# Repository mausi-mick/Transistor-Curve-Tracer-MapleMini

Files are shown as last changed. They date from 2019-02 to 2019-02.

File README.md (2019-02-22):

# Transistor-Curve-Tracer-MapleMini

This project based on the super project "Transistor Curve Tracer" from Peter Balch :
https://www.instructables.com/id/Transistor-Curve-Tracer/  

I ported the software from the 8-bit Arduino platform ( hardware: Arduino Pro Mini ) to 32 bit STM32duino (hw: MapleMini).

For me was the MapleMini the best choice: cheap, quick, enough program-space, more accessible port-pins as the Arduino Uno/Nano/... and more flexibility and accuracy :

more than 5 ADC's with 12-bit resolution, 2 SPI's/, more than 2 ISR-Pins (for the encoders) and USB-socket for programming and supply. 
Also the 3.3 V port-voltage was favourable for connections to the ILI9341-spi-tft-display/touch.

For more information about MapleMini look here: https://www.stm32duino.com/
or about this project:  https://www.stm32duino.com/viewtopic.php?t=4269

Therefore I had the possibility to integrate other features:

- integration of two rotary encoders (on isr) for a more comfortable changing of the parameters, a dual DAC (MCP4822) with the same 12-bit resolution as the ADC's on the MapleMini.
- possibility to save the parameters in the internal EEPROM
- possibility compare similar or complementary devices on the same screen
- changing x-scale for diodes/zeners (0,1,2,3,4,6,12,24V) (0: starts with 24V and search the optimal scale)
- changing y-sacle for diodes from 0...10mA  to 0...50mA
- changing y-scale for MosFETs/jFETs automatic depending on max. IDss from 50mA to 10mA or 50mA to 100mA
- changing x-scale for n-jFETs from 12V (default), 6V, 4V, 3V, 2V.

The schematic of the tracer is different from Peters version:

I use switches to connect the Emitter/Source/Cathode respectively Collector/Drain/Anode to +/- supply-voltage only while measuring - most time the DUT is only with the base connected, Emtter / Collector are isolated.
At first I tested it with a dual toggle switch, than with mechanical relais, than I changed to  PhotoMosRelais because of less space on the board and less supply-current( 40ma/5V -> 2-5mA/3.3V). So the MapleMini-ports can drive the PhotoMosRelais direct.

As amplifier to drive the Emitter/Source ... Collector/Drain I made another design.
Peter used a LM358 standard dual amplifier with emitter-followers, but I think it was difficult to make it stable and there was a big drop on the positive rail.
Therefore I searched and tested some other amplfiers with drive capacibility of more than 50mA, among others NE5532 , L2272 and TCA0372.
The TCA0372 was the best in relation to stability and to low drop on the supply (r-to-r) at 50mA.
I use only one amplifier of the TCA0372 with gain = +3 (default).
The output of the TCA0372 can manage more than 100mA, the negative supply-voltage I put down to about -3V, because the TCA0372 is not a real rail-to-rail-amplifier at this currents. The negative supply near -3V is generated with a charge-pump (from+3.3V).
With the U-DAC (MCP4822) I can generate 0...12V similar the version from Peter.
As amplifier for the base-current/gate-voltage I use a LT1013 dual amplifier, because it's a R to R and can work up to max. 44V.
The TCA0372 has a normal supply-voltage from 12.6V, changing to about 26V for measuring zeners with Vz > 12V and <= 24V. Therefore I have to change the gain of the TCA0372 to +6 (V-DAC-max  (=4.095V) * 6 >=24V).
For measuring nJFETS in the ohmic-region (< Vpinch) I can switch the x-scale at the display from 12V ... to 2V.
Between 2V and 4V the gain of the TCA0372 is switched from 3 to 2, the V-DAC MCP4822 works than from 0...2.047V with step = 0,5mV.  

The LT1013 has a positive supply-voltage from around 26V, a negative supply from -12v via a LM317L and ICL7662 charge-pump.
I need the negative supply for the gates from nJFET's and depletion-mode-nMOSFET's, the positive supply > 12V for the gates from 
p-JFET's (I think it exist only one depletion-mode-pMOSFET-chip!).

The gain of the opamp's of the LT1013 can be changed from +6 to -6 with two PhotoMosRelais, or better 
over the relais I can select the opamp with the gain +6 or -6.

For npn/pnp and MosFets the I-DAC here works from 0... 2.047 V to generate 0 ... + 12 V with gain = +6 or
with gain = -6  to generate 0 ... - 12 V gatevoltage for nJFET's,
for pJFET's the I-DAC works from about 2.048 ... 4.095 V to generate gatevoltage from +12 ... +24 V for
pJFET with gain +6.

The current is limited to max 50mA . only for JFET's/MOSFET's it can go in a second step up to about 100mA.

The software is developed with the ARDUINO IDE 1.8.4, STM32duino is about one year (2017) old, but I think the newest version would work to.

You have to load  Bootloader 2.0 (20k RAM, 120k Flash) in MapleMini.

The main components are:

- ILI9341 TFT-SPI-Display 2.8" with Touch ca 6.70 €
- MapleMini                                  3.60 €
- DACMCP4822                                 3.20 € 
- AQY212 6x                                  6.00 €
- LT1013                                     1.40 €
- TCA0372                                    1.10 €
- MT3608 3x                                  2.00 €
- Rotary Encoder 2x                          2.00 €
- nMOS switch    7x                          2.00 €    
- ICL7662 (-12V) + TSP490603(-5/-3.3V)       4.00 €
-                           SUM:            32.00 €
+ resistors, capacitors, diodes, test-sockets,                                          
+ pcb's, wire, zinn, sockets, battery, chassis ...     

The hardware is nearly finsihed, the software is growing !

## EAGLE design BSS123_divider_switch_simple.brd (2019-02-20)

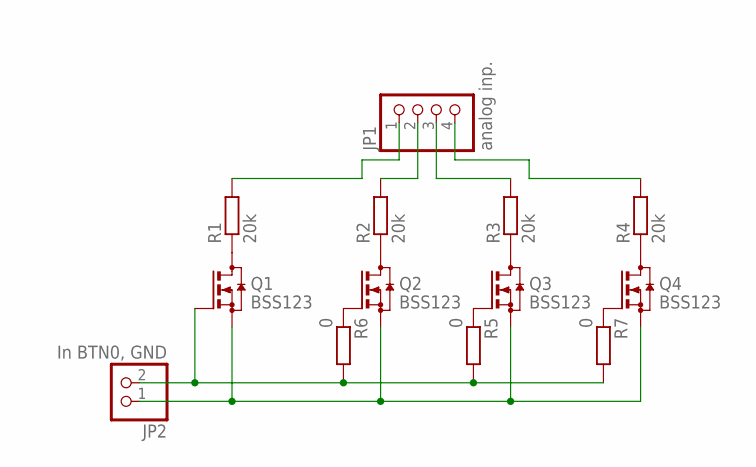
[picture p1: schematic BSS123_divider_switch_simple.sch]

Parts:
JP1: analog inp.; 1X04
JP2: In BTN0, GND; 1X02
Q1, Q2, Q3, Q4: BSS123; SOT23
R1, R2, R3, R4: 20k; R1206
R5, R6, R7: 0; R1206

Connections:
unnamed: Q1.3 (D), R1.1
unnamed: Q2.3 (D), R2.1
unnamed: Q3.3 (D), R3.1
unnamed: Q4.3 (D), R4.1
unnamed: Q4.1 (G), R7.1
unnamed: JP2.1, Q1.2 (S), Q2.2 (S), Q3.2 (S), Q4.2 (S)
unnamed: JP1.1, R1.2
unnamed: JP1.2, R2.2
unnamed: JP1.3, R3.2
unnamed: JP1.4, R4.2
unnamed: Q2.1 (G), R6.1
unnamed: Q3.1 (G), R5.1
unnamed: JP2.2, Q1.1 (G), R5.2, R6.2, R7.2

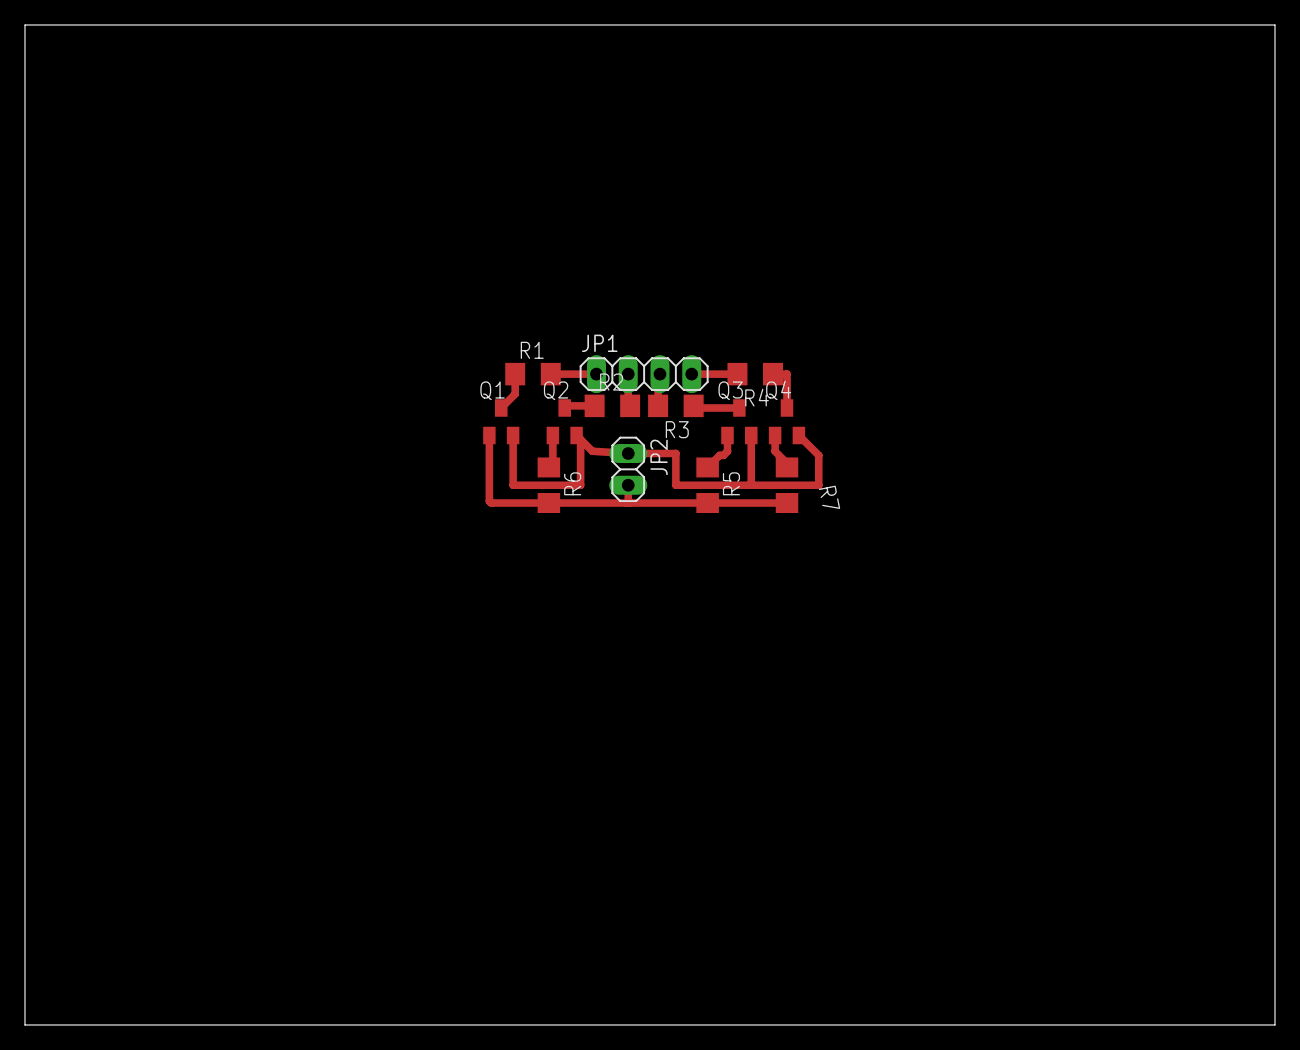
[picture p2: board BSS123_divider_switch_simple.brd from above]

Board: 2 copper layers, 100.0 x 80.0 mm, 13 parts (0 on the bottom side), 13 nets.

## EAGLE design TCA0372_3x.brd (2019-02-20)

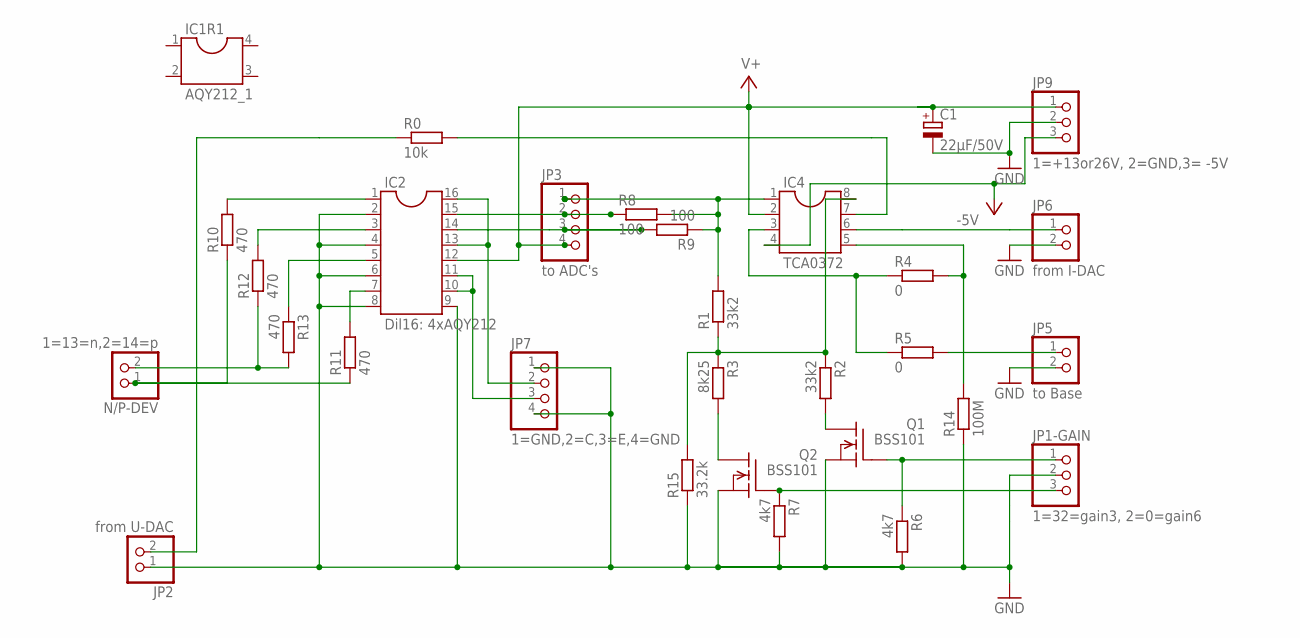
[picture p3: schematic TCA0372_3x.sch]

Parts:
C1: 22µF/50V; E5-10,5
IC1R1: AQY212_1; SOCKET-04
IC2: Dil16: 4xAQY212; SOCKET-16
IC4: TCA0372; SOCKET-08
JP1-GAIN: 1=32=gain3, 2=0=gain6; 1X03
JP2: from U-DAC; 1X02
JP3: to ADC's; 1X04
JP5: to Base; 1X02
JP6: from I-DAC; 1X02
JP7: 1=GND,2=C,3=E,4=GND; 1X04
JP9: 1=+13or26V, 2=GND,3= -5V; 1X03
N/P-DEV: 1=13=n,2=14=p; 1X02
Q1, Q2: BSS101; TO92
R0: 10k; 0207/7
R1, R2: 33k2; 0207/7
R3: 8k25; 0207/7
R4, R5: 0; 0207/7
R6, R7: 4k7; 0207/7
R8, R9: 100; 0207/7
R10, R11, R12, R13: 470; 0207/7
R14: 100M; 0207/7
R15: 33.2k; 0207/7

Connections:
-5V: IC4.4, JP9.3
GND: C1.-, IC2.2, IC2.4, IC2.6, IC2.8, IC2.9, JP1-GAIN.2, JP2.1, JP5.2, JP6.2, JP7.1, JP7.4, JP9.2, Q1.1 (S), Q2.1 (S), R6.2, R7.2, R14.1, R15.1
unnamed: IC4.5, R4.2, R14.2
unnamed: IC2.15, JP3.2, R8.1
unnamed: IC4.7, R0.2
unnamed: IC2.7, R11.2
unnamed: Q1.3 (D), R2.2
unnamed: Q2.3 (D), R3.2
unnamed: JP1-GAIN.1, Q1.2 (G), R6.1
unnamed: JP1-GAIN.3, Q2.2 (G), R7.1
unnamed: IC4.6, JP6.1
unnamed: IC2.3, R12.2
unnamed: IC2.13, IC2.16, JP7.2
unnamed: JP2.2, R0.1
unnamed: IC4.3, R4.1, R5.1
unnamed: IC2.5, R13.1
unnamed: N/P-DEV.2, R12.1, R13.2
unnamed: IC2.1, R10.2
unnamed: N/P-DEV.1, R10.1, R11.1
unnamed: JP5.1, R5.2
unnamed: IC4.1, JP3.1, R1.2, R8.2, R9.1
unnamed: IC4.8, R1.1, R2.1, R3.1, R15.2
unnamed: IC2.10, IC2.11, JP7.3
unnamed: IC2.14, JP3.3, R9.2
V+: C1.+, IC2.12, IC4.2, JP3.4, JP9.1

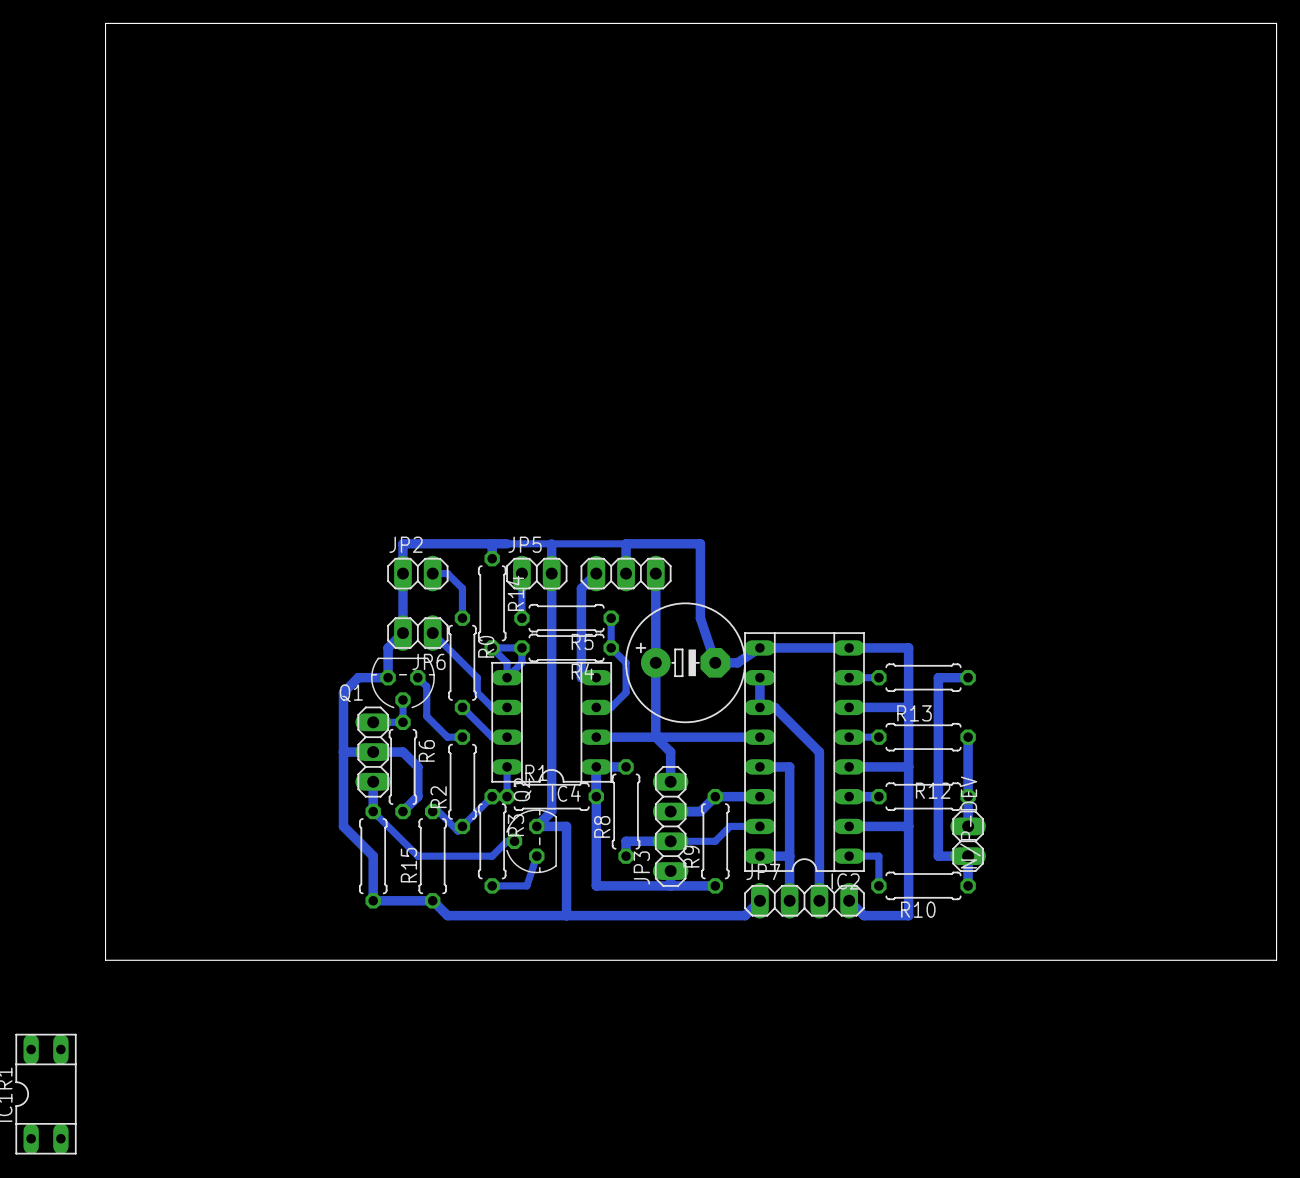
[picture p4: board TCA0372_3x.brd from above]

Board: 2 copper layers, 100.0 x 80.0 mm, 30 parts (0 on the bottom side), 25 nets.

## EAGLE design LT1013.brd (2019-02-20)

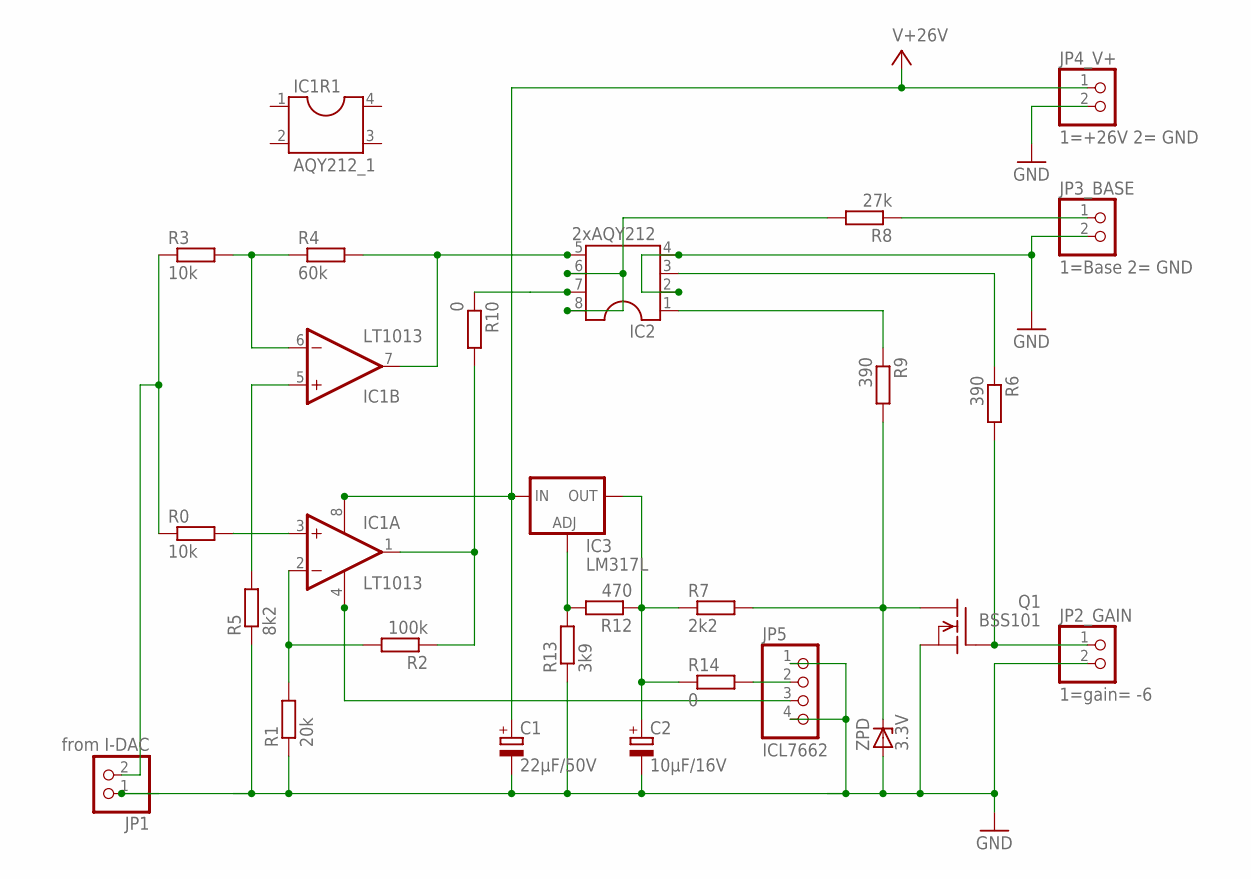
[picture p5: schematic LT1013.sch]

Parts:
C1: 22µF/50V; E5-10,5
C2: 10µF/16V; B45181B
IC1: LT1013; DIL08
IC1R1: AQY212_1; SOCKET-04
IC2: 2xAQY212; SOCKET-08
IC3: LM317L; 317L
JP1: from I-DAC; 1X02
JP2_GAIN: 1=gain= -6; 1X02
JP3_BASE: 1=Base 2= GND; 1X02
JP4_V+: 1=+26V 2= GND; 1X02
JP5: ICL7662; 1X04
Q1: BSS101; TO92
R0, R3: 10k; 0207/7
R1: 20k; 0207/7
R2: 100k; 0207/7
R4: 60k; 0207/7
R5: 8k2; 0207/7
R6, R9: 390; 0207/7
R7: 2k2; 0207/7
R8: 27k; 0207/7
R10, R14: 0; 0207/7
R12: 470; 0207/7
R13: 3k9; 0207/7
ZPD: 3.3V; ZDIO-7.5

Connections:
GND: C1.-, C2.-, IC2.2, IC2.4, JP1.1, JP2_GAIN.2, JP3_BASE.2, JP4_V+.2, JP5.1, JP5.4, Q1.1 (S), R1.1, R5.1, R13.1, ZPD.A
unnamed: IC1.6 (-IN), R3.2, R4.1
unnamed: IC1.2 (-IN), R1.2, R2.2
unnamed: IC1.1 (OUT), R2.1, R10.2
unnamed: IC1.3 (+IN), R0.2
unnamed: IC2.1, R9.1
unnamed: IC1.7 (OUT), IC2.5, R4.2
unnamed: Q1.3 (D), R7.2, R9.2, ZPD.C
unnamed: JP5.2, R14.2
unnamed: JP3_BASE.1, R8.1
unnamed: IC2.6, IC2.8, R8.2
unnamed: JP2_GAIN.1, Q1.2 (G), R6.2
unnamed: JP1.2, R0.1, R3.1
unnamed: IC1.5 (+IN), R5.2
unnamed: IC2.3, R6.1
unnamed: IC2.7, R10.1
unnamed: IC1.4 (V-), JP5.3
unnamed: IC3.1 (ADJ), R12.2, R13.2
unnamed: C2.+, IC3.2 (OUT), R7.1, R12.1, R14.1
V+: C1.+, IC1.8 (V+), IC3.3 (IN), JP4_V+.1

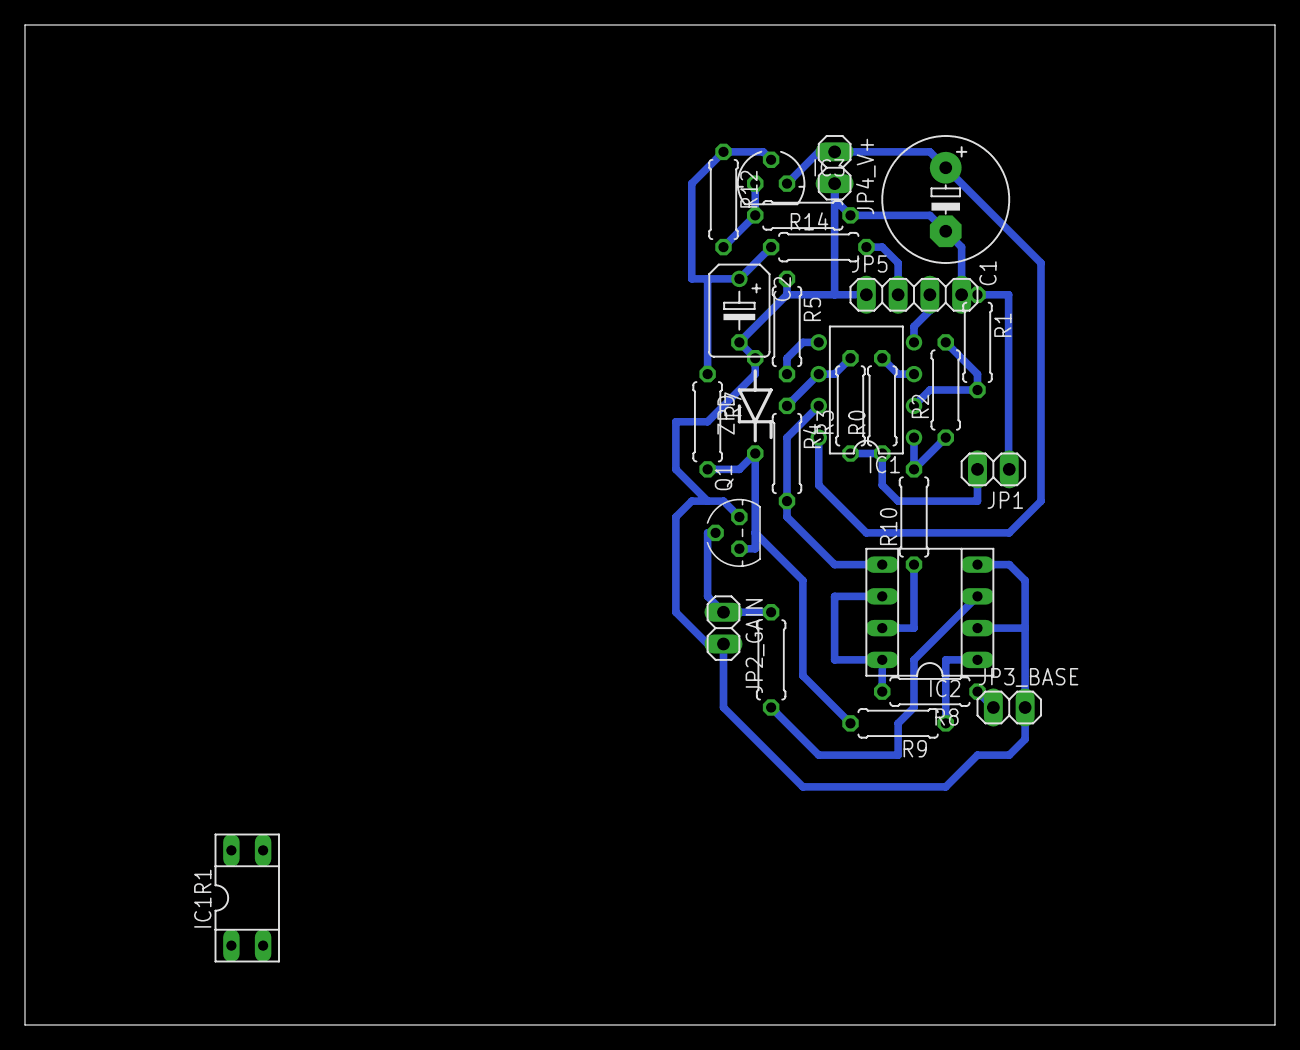
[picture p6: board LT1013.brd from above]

Board: 2 copper layers, 100.0 x 80.0 mm, 27 parts (0 on the bottom side), 20 nets.

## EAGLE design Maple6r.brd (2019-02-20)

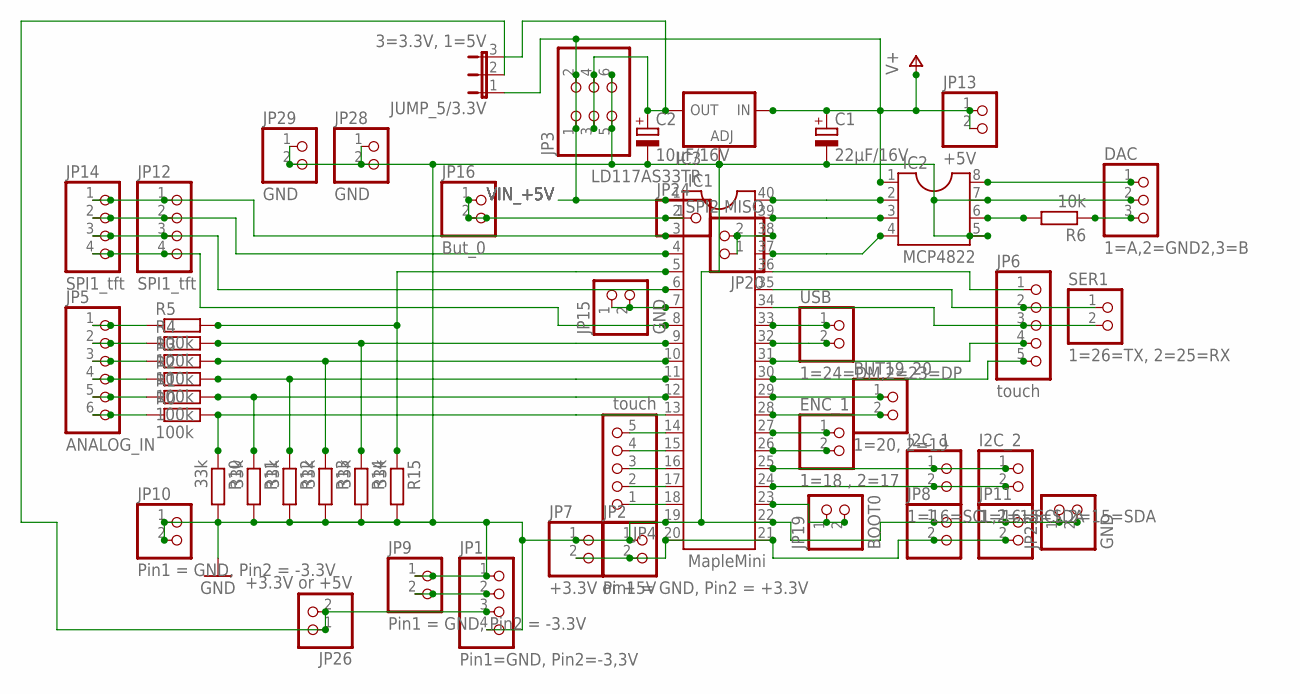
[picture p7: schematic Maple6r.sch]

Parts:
BUT19_20: 1=20, 2=19; 1X02
C1: 22µF/16V; E5-8,5
C2: 10µF/16V; E5-8,5
DAC: 1=A,2=GND2,3=B; 1X03
ENC_1: 1=18 , 2=17; 1X02
I2C_1, I2C_2: 1=16=SCL,2=15=SDA; 1X02
IC1: MapleMini; DIL40
IC2: MCP4822; SOCKET-08
IC3: LD117AS33TR; SOT223
JP1: Pin1=GND, Pin2=-3,3V; 1X04
JP2: Pin1 = GND, Pin2 = +3.3V; 1X02
JP3: PINHD-2X3; 2X03
JP4, JP6: touch; 1X05
JP5: ANALOG_IN; 1X06
JP7, JP26: +3.3V or +5V; 1X02
JP8, JP11: PINHD-1X2; 1X02
JP9, JP10: Pin1 = GND, Pin2 = -3.3V; 1X02
JP12, JP14: SPI1_tft; 1X04
JP13: +5V; 1X02
JP15, JP23, JP28, JP29: GND; 1X02
JP16: But_0; 1X02
JP19: BOOT0; 1X02
JP20: SPI2 MISO; 1X02
JP24: PINHD-1X1; 1X01
JUMP_5/3.3V: 3=3.3V, 1=5V; JP2
R0, R1, R2, R3, R4, R5: 100k; 0207/7
R6: 10k; 0207/7
R10, R11, R12, R13, R14, R15: 33k; 0207/7
SER1: 1=26=TX, 2=25=RX; 1X02
USB: 1=24=DM,2=23=DP; 1X02

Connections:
1_PB10: IC1.3, JP12.1, JP14.1
2_PB2: IC1.4, JP12.2, JP14.2
3_PB0: IC1.5, R5.2, R15.1
4_PA7: IC1.6, JP12.3, JP14.3
6_PA5: IC1.8, JP12.4, JP14.4
7_PA4: IC1.10, R3.2, R13.1
8_PA3: IC1.11, R2.2, R12.1
10_PA1: IC1.12, R1.2, R11.1
11_PA0: IC1.13, R0.2, R10.1
GND: C1.-, C2.-, DAC.2, IC1.19, IC1.22, IC2.5, IC2.7, IC3.1 (ADJ), JP1.1, JP1.4, JP2.1, JP3.5, JP3.6, JP7.1, JP8.1, JP9.1, JP10.1, JP10.2, JP11.1, JP23.1, JP23.2, JP28.1, JP28.2, JP29.1, JP29.2, R10.2, R11.2, R12.2, R13.2, R14.2, R15.2
unnamed: IC1.9, R4.2, R14.1
unnamed: JP5.1, R5.1
unnamed: JP5.2, R4.1
unnamed: JP5.3, R3.1
unnamed: JP5.4, R2.1
unnamed: JP5.5, R1.1
unnamed: JP5.6, R0.1
unnamed: IC1.30, JP6.5
unnamed: IC1.7, JP15.1, JP15.2
unnamed: IC1.32, USB.2
unnamed: IC1.2, JP16.1, JP16.2, JP24.1
unnamed: IC1.31, JP6.4
unnamed: JP1.2, JP9.2
unnamed: ENC_1.1, IC1.27
unnamed: JP1.3, JP26.1, JP26.2, JUMP_5/3.3V.2
unnamed: IC1.38, JP20.1, JP20.2
unnamed: IC1.33, USB.1
unnamed: IC1.36, JP6.1
unnamed: IC1.35, JP6.2, SER1.1
unnamed: IC2.6, R6.2
unnamed: IC1.40, IC2.2
unnamed: IC1.39, IC2.3
unnamed: IC1.14, JP4.5
unnamed: IC1.37, IC2.4
unnamed: IC1.15, JP4.4
unnamed: C2.+, IC3.4 (OUT), JP3.3, JP3.4, JUMP_5/3.3V.3
unnamed: IC1.34, JP6.3, SER1.2
unnamed: IC1.16, JP4.3
unnamed: IC1.17, JP4.2
unnamed: IC1.18, JP4.1
unnamed: BUT19_20.1, IC1.29
unnamed: BUT19_20.2, IC1.28
unnamed: ENC_1.2, IC1.26
unnamed: I2C_1.1, I2C_2.1, IC1.25
unnamed: I2C_1.2, I2C_2.2, IC1.24
unnamed: IC1.23, JP19.1, JP19.2
unnamed: IC1.20, IC1.21, JP2.2, JP7.2, JP8.2, JP11.2
unnamed: DAC.3, R6.1
unnamed: DAC.1, IC2.8
VIN_+5V: C1.+, IC1.1, IC2.1, IC3.3 (IN), JP3.1, JP3.2, JP13.1, JP13.2, JUMP_5/3.3V.1

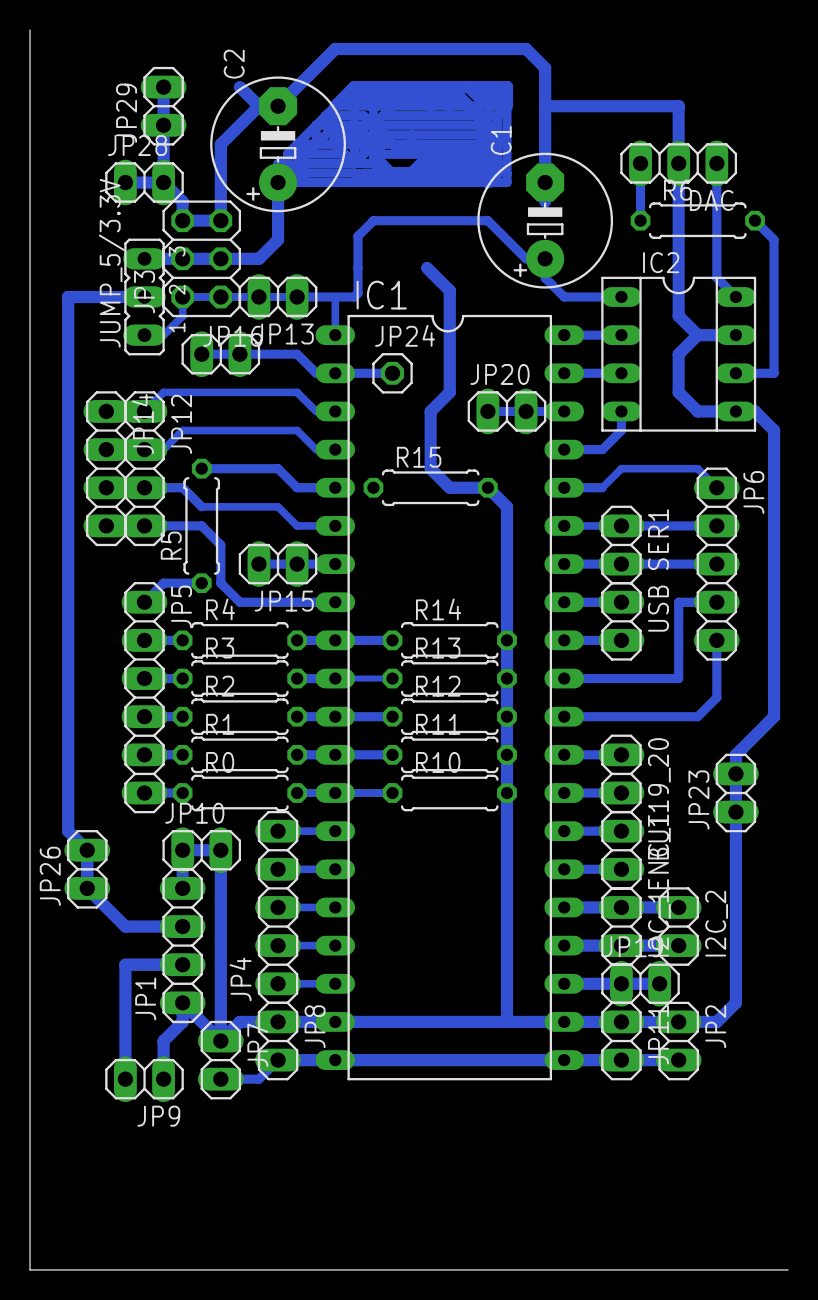
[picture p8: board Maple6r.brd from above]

Board: 2 copper layers, 50.5 x 82.5 mm, 49 parts (1 on the bottom side), 50 nets.

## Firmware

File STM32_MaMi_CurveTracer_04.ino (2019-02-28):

//
// 2018.11.18 Changed enc2 PINs from 19,20  ...> 15,16, because 20 is no isr-pin digitalWrite(BTN32, LOW);
// 2018.11.27 s_comp for compare DUT's (or cmplements) on screen
// 2018.11.28 test switch over relais              ?? ok, ADC4 free
// 2018.11.29 test switch over photo-relais AQY212 ?? ok, ADC4 free
// 2018.11.30 test current-limit with ADC3 and ADC2/ADC1 and R32/R37 = 100 Ohm, cleaning program
// 2018.12.01 EEProm read in setup ( test only, deactivated on 2018.12.05)
// 2018.12.05 test n-JFET with neg Vgs with ICL7662 and inv. opamp TL062 (input from MCP4822 DAC-A)
// 2018.12.12 changed TL062 with LT1013, because he works with maximal 44V (preparing for p-FET and perhaps Zener:
//            LT1013 : -13V (ICL7662) and + 26V (13V supply + ICL7662 as doppler))
// 2018.12.14 Dacbase auf 0...2.048V wegen LT1013 an -13...+26V (other divider on + output (100k/20k -> gain = 6)
// 2018.12.14 Curve_MapleMi_14 intgrrate zener over LT1013 (PIN7) 26V and ADC4 with Rz to ground
// 2018.12.18 Curve_MapleMi_15 : test p-JFET with ScanAllNeg_pJFET and Base = 26V .... 13V
//                               integrate ScanAllNeg_PJFET in ScanAllNeg
// 2018.12.22 test diodes 0V...24V and pJFET > 50mA
// 2018.12.26 STM32_MaMi_PinTest_00: chnnge BTN1 to BTN0 (Pin0), SPI1_NSS_PIN (to Pin1), TFT_DC (to Pin2),Pin15,16 (I2C) free
//            test -3.3V on pin5 TCA0372 (instead of 0V) better in Zero-area, test spikes / cntv
// 2019.01.05 STM32_MaMi_CurveTracer_00: copy from STM32_MaMi_PinTest_00 without scanzener ...
// 2018.01.10 STM32_MaMi_CurveTracer_01: copy from ..._ , but gain TCA0372 for I-DAC from 3 to 6 (all devices with DAC 0...2.047V , only for pJFET with 2.047...4.096 for 12 ...24V gate-Voltage)...
// 2018.01.10                            V_bat reduce to 12.5V (beacause 13.6V was to much for the ADC (with divider 100K33k) problems with pn-diodes (Uz to small)
// 2018.01.16                            LT1013 on separate MT3608 with 26V, neg supply with LM317 (+12V) and ICL7662-board (ca -12V)
// 2018.01.23 STM32:MaMi_CurveTracer_03: Parameters from EEPROM , possibility to save the three x 4  parameters there.
// 2018.01.25                            New Menu with better separation start buttons "P" and "N" and more space for the parameters and EEPROM-Savings.
// 2019.02.17 STM32_MaMi_CurveTracer_04: aus 02xx: new pins for ENC2, BTN13/BTN14, better graphic 
// 2019.02.19                            Scan nJFET with Vds 2V,3V,4V,6V and 12V, easier update C4-parameter like c4_DIO, c4_FET with polling count3 
// 2019.02.22                            show simulated resistances in trces from p- and n-JFETs. 
 
#include <EEPROM.h>

#include <SPI.h>
//
// ### MapleMini Pin definitions   ###############################################

#define BTN0              0   // PB11 PWM// BTN0 switch gain to 6, bat-voltage from 12 to 24V and divider from 100/33 to 100/(33||20) ###
#define SPI1_NSS_PIN      1   // PB10 PWM// SPI1: TFT_CS, SPI1 : d   
#define TFT_DC            2   // PB2     // SPI1: switch data/control , default: BOOT1  for boot with RS232
#define pin_ADC5_Bat_3V   3   // PB0  PWM// ADC5 read battery-voltage fo alarm ??? <-- open 
//      TFT_MOSI          4   // PA7  PWM// SPI1 intern for TFT ILI9341
//      TFT_MISO          5   // PA6  PWM// SPI1 intern, not used, for instance SD-Read
//      TFT_SCK           6   // PA5     // SPI1 intern for TFT ILI9341
#define pin_ADC4          7   // PA4     // ADC4 --- free ### normal: SPI1_SS_PIN  to PIN12 / PC15 
#define pin_ADC3_Bat_12V  8   // PA3  PWM// ADC3
#define pin_ADC2_Vc_PNP   9   // PA2  PWM// ADC2
#define pin_ADC1_Vc_NPN  10   // PA1  PWM// ADC1
#define pin_ADC0_Vo_OPV  11   // PA0     // ADC0  // V-output TCA0372 (PIN1)

#define BTN12            12   // PC15    // BTN12 Switch for changing gain amplifiers LT1013 (- for nJFET's, + for the others)
#define BTN13            13   // PC14    // BTN13 Switch for relais to activate npn,nMOS,nDiode,n-jFET ---> Scan_n_Dev
#define BTN14            14   // PC13    // BTN14 Switch for relais to activate pnp,pMOS,pDiode,p-jFET ---> Scan_p_Dev
// boot0                BUT   // PB8     // BOOT0
//                       15   // PB7  PWM// --- yet not used ----  default:  I2C_1 SDA
//                       16   // PB6  PWM// --- yet not used ----  default:  I2C_1 SCL
//                       17   // PB5     // ENC1 Inp A
//                       18   // PB4     // ENC1 Inp B
//                       19   // PB3     // ENC2 INP A
//                       20   // PA15    // ENC2 INP B
//TOUCH IRQ              21   // PA14    // Touch irq
//TOUCH DOUT             22   // PA13    // Touch dout
//                       23   // PA12    // --- intern USB_DP
//                       24   // PA11 PWM// --- intern USB_DM
//Touch DIN              25   // PA10 PWM// Touch din
//Touch CS               26   // PA9  PWM// Touch cs
//Touch CLK              27   // PA8  PWM// Touch clk
//SPI2_MOSI              28   // PB15 PWM// SPI2_MOSI intern for DAC MCP48x2
//SPI2_MISO              29   // PB14 PWM// SPI2_MISO intern, not used
//SPI2_SCK               30   // PB13 PWM// SPI2_SCK  intern for DAC MCP48x2
#define SPI2_NSS_PIN     31   // PB12    // SPI2_CS   ( You can change it to the STM32 pin you want).
#define BTN32            32   // PB8     // switch gain to 3 ,(bat-voltage = 12V (normal)), default : BOOT0 for boot RS232
#define BOARD_LED        33   // PB1     // Pin33 / PB1 on MapleMini not outside 
#define TFT_RST         112   // ??      // formal, in reality on 3.3V 

SPIClass SPI_2(2);        // Create an instance of the SPI Class called SPI_2 that uses the 2nd SPI Port+
byte data;

/* // MCP48x2 DAC PIN-Map ##########################
  //
  //Vdd + 1      8 Vout A  ("Base")
  //CS    2      7 Vss  -
  //SCK   3      6 Vout B  ("Vcc");
  //SDI   4      5 LDAC ( on Vss/-)
  //
*/

#include <Adafruit_GFX_AS.h>
#include <Adafruit_ILI9341_STM.h>

Adafruit_ILI9341_STM tft = Adafruit_ILI9341_STM(SPI1_NSS_PIN, TFT_DC);//, TFT_RST); // Using hardware SPI (SPI_1

#include <URTouch.h>

//URTouch(      clk,cs,din,dout,irq);
URTouch  myTouch( 27, 26, 25, 22, 21);      //  <<-   24,  23 reserved for USB !!
//URTouch  myTouch(PA8,PA9,PA10,PA13,PA14); //  <<- PA11,PA12 reserved for USB !!

//### from multiencoder / madias ##################  // STM32duino
#define MAXENCODERS 2
volatile int encstate[MAXENCODERS];
volatile int encflag[MAXENCODERS];
boolean A_set[MAXENCODERS];
boolean B_set[MAXENCODERS];
volatile int16_t encoderpos[MAXENCODERS];
volatile int  encodertimer = millis(); // acceleration measurement


int encoderpinA[MAXENCODERS] = {17,19}; // pin array of all encoder A inputs encoder 0,1  // PB5,PB3
int encoderpinB[MAXENCODERS] = {18,20}; // pin array of all encoder B inputs encoder 0,1  // PB4,PA15
unsigned int lastEncoderPos[MAXENCODERS];

#include <Wire.h>     // Use the Wire Library for I2C ###########################  not used, only tested

//uint8_t enc0dir = 0;  // Drehrichtung 0=left, 1=right
//uint8_t enc1dir = 0;  // Drehrichtung

uint8_t s_func = 0, s_diode = 0, s_npn = 0, s_pnp = 0, s_fet = 1, s_depl = 0, s_dio = 0;
volatile uint8_t s_comp = 0;
uint8_t s_first = 1, s_touch = 0, s_save = 0, s_trace = 0, s_start = 1, s_auto = 0, s_flat = 0;
uint8_t s_pinch = 0, s_jfet = 0, s_ndiode = 0, s_pdiode = 0, s_vgate0 = 0, s_tend = 0, zen_v = 0, fet_v = 0;    // Z??
int8_t s_secy = 0, s_secx = 0, s_exec_npn = 0, s_exec_pnp = 0, s_graph0;
int s_yfactor = 1, s_xfactor = 1;
int pinch_v = 0, cntv = 0;
int n = 0;

byte a = 0;              // Variable to store the Byte from I2C
//char buffer0[9];         //the ASCII of the integer will be stored in this char array
//char buffer1[9];         //the ASCII of the integer will be stored in this char array

#define TFT_WIDTH     320
#define TFT_HEIGHT    240
#define GRID_WIDTH    300
#define GRID_HEIGHT   210


const int TextLeft  = 40;
const int TextTop   = 56 + 10 + 4;
const int ValLeft   = 148;
const int BoxTop    = 48;
const int BoxLeft   = 176;
const int RowHeight = 50;

const int OKWidth   = 87;
const int OKHeight  = 34;
const int OKLeft    = (TFT_WIDTH - OKWidth);// 233
const int OKTop     = 1; //5 ## displ TFT_HEIGHT - OKHeight - 8; // #?

const int DiodeLeft   =   0; // 20;  // ### di
const int BIPOLLeft   =  80; // 10;
const int MOSFETLeft  = 160; //114;
const int JFETLeft    = 240; //218;

const int ADC_MAX = 4096; // maple mini // 1024; // arduino NANO
const int DAC_MAX = 4096; // MCP4822=4096, MCP4812=1024, MCP4802 = 256
int amax, dmax, dhalf,dacv_max;

const int R1 = 33;  // 3.3V Ref // 1.1V Ref  22; // 33; //ADC input potential divider lower resistor k-ohms  ###
const int R2 = 100; // 3.3V Ref // 1.1V Ref 258; // 58; // 58; for 3.6V ; 47; // ADC input potential divider upper resistor k-ohms  ###
const int R3 = 100; // collector resistor ohms
const int R4 = 68;  //50;  // 68; ### // DAC op amp feedback upper resistor k-ohms ###############################################################
const int R5 = 33;  //26;  // 33; ### // DAC op amp feedback lower resistor k-ohms ###############################################################
const int R6 = 10;  // 3.3V Ref // 1.1V Ref 85;  // 10; // measure battery volts potential divider upper resistor k-ohms
const int R7 = 33;  // 3.3V Ref // 1.1V Ref 22;  // 33; // measure battery volts potential divider lower resistor k-ohms

const int DacVref = 40; // DAC Vref in 100s of mV
const int AdcVInt = 33; // ADC Vref in 100s of mV (Arduino UNO/NANO: INTERNAL 1.1 V)
const int AdcVref = 5;  // ADC Vref in V  ### test ???
const int mAmax   = 50; // Ic for top of screen
const unsigned long TimeoutPeriod = 60000;

volatile int16_t count2 = 0, count3 = 0, count2_a = 999, count3_a = 999; // ### e
volatile uint32_t lastEnc3 = 0, currMill3 = 0;           // ### e
volatile uint32_t lastEnc2 = 0, currMill2 = 0;           // ### e


int minNPNa = 0, incNPNa = 20, maxNPNa; //,minNPNbasea=10,incNPNbasea=10;  // ### e
int minFETa = 10, incFETa = 1, maxFETa; //,minFETvolta=10,incFETvolta=10;  // ### e
int minMOSa = 10, incMOSa = 1, maxMOSa; //,minMOSvolta=10,incMOSvolta=10;  // ### e
int maxDIOa = 5, incDIOa = 0, minDIOa; //.minAnodea=5,incAnodea=1;
int16_t c2_BIP, c2_DIO, c2_FET, c2_MOS = 0;
int16_t c3_BIP, c3_DIO, c3_FET, c3_MOS = 0;
int16_t c4_BIP, c4_DIO, c4_FET, c4_MOS = 0;
int16_t i_3V=0,i_7V = 0;

//int Adc_12V  = 0;  // test
int DacVcc;
int MinVgate = 10;
int MaxVgate = 120;  // 12 ###
int IncVgate = 1;   // 100mV ? ### e
int MinV_FET = 10;
int MaxV_FET = 120;  // 12 ###
int IncV_FET = 1;   // 100mV ? ### e
int MinV_MOS = 10;
int MaxV_MOS = 120;  // 12 ###
int IncV_MOS = 1;   // 100mV ? ### e
int MinIbase = 0;  //20;#############################################
int MaxIbase = 0; // 400 350; ### e µA #############################
int IncIbase = 20;  // ### e
int MinIanode = 0;  //5 ###############################################
int IncIanode = 0; // ### di max-voltage
int MaxIanode = 5;  // ### di test
long ngJFET = dmax; // 12 bit 4095
long iiold = 0;

int minYposGain, maxYposGain, minBaseGain, maxBaseGain; // used when calc gain

int iaz = 0, iu0 = 0, iu1 = 0, iu2 = 0, iu3 = 0, iuz, val = 0; // ### di
int16_t xt = 0, yt = 0;
int prev_x = 0, prev_y = 0;
long ils = 0;
float izf = 0, uz = 0, fro = 0, f_thrn = 0, f_thrp = 0;

// FLASH memory address defines ####### EEPROM ########
#define PREAMBLE_VALUE  2859

#define PARAM_PREAMBLE  0
#define PARAM_C2_BIP    1
#define PARAM_C3_BIP    2
#define PARAM_C4_BIP    3
#define PARAM_C2_MOS    4
#define PARAM_C3_MOS    5
#define PARAM_C4_MOS    6
#define PARAM_C2_FET    7
#define PARAM_C3_FET    8
#define PARAM_C4_FET    9
#define PARAM_C2_DIO   10
#define PARAM_C3_DIO   11
#define PARAM_C4_DIO   12

#define PARAM_ZERO1    13
#define PARAM_ZERO2    14
#define PARAM_ZERO3    15
#define PARAM_ZERO4    16
#define PARAM_ZERO5    17
#define PARAM_ZERO6    18


// TFT display constants
#define PORTRAIT      0
#define LANDSCAPE     1

// display colours
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
